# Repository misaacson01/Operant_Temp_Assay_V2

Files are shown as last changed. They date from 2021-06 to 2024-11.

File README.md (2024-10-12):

# Operant_Temp_Assay_V2

This repo contains code and instructions for assembling, installing, and operating the Hoon lab operant temperature apparatus (V2). This is an updated and modified version of the assay originally described by [Isaacson and Hoon, 2021](https://doi.org/10.1177/17448069211013633).

## Hardware assembly
1) Order two recirculating water baths with external recirculation ports, such as [this one](https://www.polyscience.com/products/circulating-baths/refrigeratedheated-circulating-baths/refrigerated-circulator-7-liter-low-profile-sd-20-c).
2) Order all tubing, parts, and electronics according to the [parts list](https://github.com/misaacson01/Operant_Temp_Assay_V2/blob/main/Parts%20List.xlsx).
3) Order all custom 3D printable parts listed in the [parts list](https://github.com/misaacson01/Operant_Temp_Assay_V2/blob/main/Parts%20List.xlsx). Stl files needed to print the parts can be found in the [3D Prints](https://github.com/misaacson01/Operant_Temp_Assay_V2/tree/main/3D%20prints) folder.
    * To order custom prints online, use a 3D print service such as [Craftcloud](https://craftcloud3d.com/) by uploading the .stl files located in the [3D Prints folder](https://github.com/misaacson01/Operant_Temp_Assay_V2/tree/main/3D%20prints).
    * To print the parts yourself, we recommended using an FDM printer such as the [Prusa MK4S](https://www.prusa3d.com/product/original-prusa-mk4s-3d-printer-5/) using PLA filament.
    * Whether going through a service or printing yourself, these are our suggested print parameters:
        * File units: millimeters
        * Printing process type: FDM
        * Material: PLA
        * Infill: 20%
        * Support: none
        * Layer Height: 300 micrometers (or less)
        * Finish: Standard/As printed/No finish
        * Print orientation: default
        * Tolerance: 500 micrometers (or less)
4) Assemble the nose poke detectors
    * Solder the photo interrupter, a 200 Ohm resistor, and ~0.5 m each of 3 hookup wires (red=power, black=ground, and yellow=signal) to the photo interrupter breakout PCB. Repeat this step to create 3 assembled photointerrupter-based nose poke detectors
    * Place each nose poke detector into the matching slots of the Thermobox 3D print. Add a dab of glue to fix the detectors in place
5) Assemble the water bath valves and large tubing
    * Connect 1/4" hose barb connectors to both sides of 2 large solenoid valves (2 valves are used for the two water bath circulating loops)
    * Hook up water baths, large (8 mm ID) tubing, and large valves according to page 1 of the [tubing diagram](https://github.com/misaacson01/Operant_Temp_Assay_V2/blob/main/docs/Thermo%20Assay%20V2%20Diagrams.pptx)
    * Connect the large solenoid valves to power according to page 2 of the [tubing diagram](https://github.com/misaacson01/Operant_Temp_Assay_V2/blob/main/docs/Thermo%20Assay%20V2%20Diagrams.pptx)
6) Assemble the water bath small tubing
    * Using the ThermoTemplate 3D print, wind the copper tubing into the slots of the template to bend the copper tubing into a shape of a regularly-spaced grid. Remove the copper tubing from the template when finished
    * Connect the copper tubing to the small valves according to page 1 of the [tubing diagram](https://github.com/misaacson01/Operant_Temp_Assay_V2/blob/main/docs/Thermo%20Assay%20V2%20Diagrams.pptx)
    * Connect the small tubing to the large tubing according to page 1 of the [tubing diagram](https://github.com/misaacson01/Operant_Temp_Assay_V2/blob/main/docs/Thermo%20Assay%20V2%20Diagrams.pptx), using the reducer adapters (8 mm to 6 mm, 1/4" to 1/8") and tubing (1/4" ID)
    * Connect the small solenoid valves to power according to page 2 of the [tubing diagram](https://github.com/misaacson01/Operant_Temp_Assay_V2/blob/main/docs/Thermo%20Assay%20V2%20Diagrams.pptx)
    * Slide the copper tubing grid into the floor slot of the Thermobox
7) Assemble the liquid reward delivery tubing
    * Connect a water reservoir (e.g. a large syringe tube) to the masteflex tubing
    * Glue the 1/8" to 1/16" adapters to the underside of each of the reward ports, with the smaller (1/16") end pointing up into the port to create a reward spout
    * Mount the water reservoir 6-12" above the height of the reward spouts (liquid rewards are gravity-fed)
    * Connect 1/8" hose barb connectors to both sides of 3 small solenoid valves (3 valves are used for 3 separate reward locations in the Thermobox)
    * Use Tee connectors to split the tubing from the reservoir to connect to one port the 3 small solenoid valves
    * Connect the opposite ports of each small solenoid valve to each of the reward spouts adapters
8) Wire the liquid reward delivery valves (see also page 2 of the [tubing diagram](https://github.com/misaacson01/Operant_Temp_Assay_V2/blob/main/docs/Thermo%20Assay%20V2%20Diagrams.pptx))
    * Using black hookup wire, connect the negative (ground) screw terminal of the 2.1 mm power jack to the center screw terminal of a relay in the relay module
    * Using another black wire, connect the "normally open" screw terminal of the relay to one of the two pins of a small solenoid valve (the wire may need to be soldered to the solenoid valve pin)
    * Using a red wire, connect the other pin of the solenoid valve to the positive (power) screw terminal of the 2.1 mm power jack
    * Solder a diode between the two pins of the small solenoid valve, orienting the diode so that current can flow from the negative pin to the positive pin
    * Repeat these steps for all 3 liquid reward valves
    * Plug in a 12 V (1+ A) power cord to the 2.1 mm power jack
9) (optional) Assemble the LED display boards
    * [displays are deprecated, to be replaced with newer I2C displays such as [this one](https://www.adafruit.com/product/4741)]

## Electronics assembly
[To be added]

## Software Installation

##### Install software on the host PC
1) Install [Matlab](https://www.mathworks.com/products/matlab.html)
2) Download this repository's code (with Github Desktop or your preferred SVN client)
3) Open Matlab and add this repository to the list of paths:
    * In Matlab's "Home" tab, click "Set Path"
    * Click "Add with Subfolders"
    * Navigate to the file location where this repository was downloaded and click on the folder name
    * "Save" and "Close"
4) Install the [Arduino IDE](https://www.arduino.cc/en/software).
5) Open the Arduino IDE, click "Tools", then "Manage libraries". Install the following libraries: Adafruit MAX31856; Adafruit GFX; Adafruit Seesaw; Adafuit ST7735 and ST7789; Adafruit BUSIO

##### Install the Arduino controller firmware
1) Plug in the Arduino microcontroller connected to the apparatus to the host PC.
2) Open the Arduino IDE
3) Select "Arduino Uno" from the microcontroller dropdown menu, and select the port which your Arduino is connected to
    * if you don't know which port the Arduino is on, try disconnecting the Arduino to see which port disappears
4) Download the controller.ino file from the [Arduino](https://github.com/misaacson01/Operant_Temp_Assay_V2/tree/main/Arduino) folder and load it in the Arduino IDE
5) Upload the code to the Arduino

##### Test the software installation
1) In the Matlab command window, type "edit TV2_Test_Experiment"
2) In Matlab's "Editor" tab, click "Run"
3) Watch the command window and the apparatus to check that everything is working correctly

## Running an experiment
To be added

## Troubleshooting
To be added

## Updating Arduino code
To be added

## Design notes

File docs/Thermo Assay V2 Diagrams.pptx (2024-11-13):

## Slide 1

Tubing diagram

Reducer

Large Tee connector

Bloop

Large Tee connector

Big tubing

Water bath B IN

Small tubing

Big valves

Small valves

Bout

Thermo box

Copper tubing

Water bath B OUT

Water bath A IN

T connector

Aout

Reducer

Bin

T connector

Ain

Reducer

Large Tee connector

Aloop

Large Tee connector

Water bath A OUT

Reducer

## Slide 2

Solenoid valve
wiring layout

(All solenoid valves are similarly wired)

+

Solenoid valve

Flyback diode

12 v DC

NO

relay

COM

NC

NO = normally open
COM = common
NC = normally closed

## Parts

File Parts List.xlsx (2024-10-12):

 | Part Name | URL | Catalog # | Supplier | Quantity | Price (each) | Total Cost | Notes
Tubing and valves | Masterflex L/S® Precision Pump Tubing, Platinum-Cured Silicone, L/S 16; 25 ft | https://us.vwr.com/store/item/NA5144597/masterflex-l-s-precision-pump-tubing-platinum-cured-silicone-avantor | MFLX96410-16 | VWR | 1 | $108.00 | $108.00
 | Copper Tubing, 3mm OD, 2mm ID, 16 ft Length | Refrigeration Tubing Copper Tubing Coil 3mm OD x 2mm ID x 24.5Ft Length - Walmart.com - Walmart.com (https://www.walmart.com/ip/Refrigeration-Tubing-Copper-Tubing-Coil-3mm-OD-x-2mm-ID-x-24-5Ft-Length/426649156?wmlspartner=wmtlabs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) |  | Walmart | 1 | $17.32 | $17.32
 | 8 mm ID Tubing, 50 ft length | https://www.mcmaster.com/5233K958/ | 5233K958 | McMaster-Carr | 1 | $91.50 | $91.50
 | 1/8" hose barb Tee connector | https://www.mcmaster.com/91355K57/ | 91355K57 | McMaster-Carr | 2 | $9.78 | $19.56 | qty: 2 packs of 2 (2+2 spare)
 | 8 mm ID tubing Tee connector | https://www.mcmaster.com/2429K56/ | 2429K56 | McMaster-Carr | 5 | $2.42 | $12.10 | qty: 4+spare
 | 1/8" to 1/16" hose barb adapter (for liquid reward port) | https://www.mcmaster.com/5117K52/ | 5117K52 | McMaster-Carr | 1 | $10.98 | $10.98 | qty: 1 pack of 10 (3+7 spare)
 | 1/4" to 1/8" hose barb adapter (for reducer) | https://www.mcmaster.com/91355K31/ | 91355K31 | McMaster-Carr | 1 | $13.26 | $13.26 | qty: pack of 5 (2+3 spare)
 | 8 mm to 6 mm (~1/4") hose barb adapter (for reducer) | https://www.mcmaster.com/5218K434/ | 5218K434 | McMaster-Carr | 3 | $0.58 | $1.74 | qty: 2+spare
 | 1/4" ID tubing (for reducer) | https://www.mcmaster.com/5233K56/ | 5233K56 | McMaster-Carr | 1 | $10.50 | $10.50
 | 1/4" NPT to 8mm ID hose barb adapter | https://www.mcmaster.com/2429K16/ | 2429K16 | McMaster-Carr | 8 | $4.62 | $36.96 | qty: 6+2 spare
 | 1/8" NPT to 1/8" ID hose barb adapter | https://www.mcmaster.com/5463K438/ | 5463K438 | McMaster-Carr | 1 | $14.08 | $14.08 | qty: pack of 10 (8+2 spare)
 | 12VDC 1/4" NPT Electric Solenoid Valve Normally Open (large valves) | https://www.amazon.com/SNS-2WK025-N08-Electric-Solenoid-Normally/dp/B07SPK59LP/ |  | Amazon | 3 | $20.99 | $62.97 | qty: 2+spare
 | 12VDC 1/8" NPT Electric Solenoid Valve Normally Closed (small valves) | https://www.amazon.com/Brass-Electric-Solenoid-Normally-Closed/dp/B01M5IXT4D/ |  | Amazon | 8 | $7.86 | $62.88 | qty: 7+spare
Electronics | SainSmart 8-Channel Relay Module | https://www.amazon.com/SainSmart-101-70-102-8-Channel-Relay-Module/dp/B0057OC5WK | B0057OC5WK | Amazon | 1 | $11.99 | $11.99
 | Photo Interrupter - GP1A57HRJ00F | https://www.sparkfun.com/products/9299 | SEN-09299 | Sparkfun | 4 | $2.50 | $10.00 | qty: 3+spare
 | SparkFun Photo Interrupter Breakout Board - GP1A57HRJ00F | https://www.sparkfun.com/products/9322 | BOB-09322 | Sparkfun | 4 | $1.50 | $6.00 | qty: 3+spare
 | Hook-up Wire - Black (22 AWG) | https://www.sparkfun.com/products/8022 | PRT-08022 | Sparkfun | 1 | $2.50 | $2.50
 | Hook-up Wire - Red (22 AWG) | https://www.sparkfun.com/products/8023 | PRT-08023 | Sparkfun | 1 | $2.50 | $2.50
 | Hook-up Wire - Yellow (22 AWG) | https://www.sparkfun.com/products/8024 | PRT-08024 | Sparkfun | 1 | $2.50 | $2.50
 | Adafruit METRO 328 - Arduino Compatible - with Headers - ATmega328 | https://www.adafruit.com/product/2488 | 2488 | Adafruit | 1 | $17.50 | $17.50
 | Proto-Screwshield (Wingshield) R3 Kit for Arduino | https://www.adafruit.com/product/196 | 196 | Adafruit | 1 | $14.95 | $14.95
 | (optional display) 2.2" 18-bit color TFT LCD display with microSD card breakout | https://www.adafruit.com/product/1480 | 1480 | Adafruit | 2 | $24.95 | $49.90
 | (optional display controller) Adafruit Metro Mini 328 - Arduino-Compatible - 5V 16MHz | https://www.adafruit.com/product/2590 | 2590 | Adafruit | 2 | $12.50 | $25.00
 | Adafruit Universal Thermocouple Amplifier MAX31856 Breakout | https://www.adafruit.com/product/3263 | 3263 | Adafruit | 1 | $17.50 | $17.50
 | Thermocouple Type-K Glass Braid Insulated - K | https://www.adafruit.com/product/270 | 270 | Adafruit | 2 | $9.95 | $19.90 | qty: 1+spare
 | Premium Female/Male 'Extension' Jumper Wires - 40 x 6" (150mm) | https://www.adafruit.com/product/826 | 826 | Adafruit | 1 | $3.95 | $3.95
 | 12V 5A switching power supply | https://www.adafruit.com/product/352 | 352 | Adafruit | 1 | $24.95 | $24.95
 | Female DC Power adapter - 2.1mm jack to screw terminal block | https://www.adafruit.com/product/368 | 368 | Adafruit | 1 | $2.00 | $2.00
 | USB cable - USB A to Micro-B - 3 foot long | https://www.adafruit.com/product/592 | 592 | Adafruit | 4 | $2.95 | $11.80
 | USB Mini Hub with Power Switch | https://www.adafruit.com/product/2998 | 2998 | Adafruit | 1 | $4.95 | $4.95
Test Chamber | Plymor Clear Acrylic Square Polished Edge Display Base, 0.25" H x 4" W x 4" D | https://www.amazon.com/Plymor-Acrylic-Polished-Display-Base-25/dp/B013ITD132 | B013ITD132 | Amazon | 1 | $8.46 | $8.46
 | 3D prints - Test Chamber, Catch Tray, Tube Template | https://craftcloud3d.com/ | - | Craftcloud3d | 1 | $50.00 | $50.00 | cost estimate
 |  |  |  |  |  | Total | $748.20

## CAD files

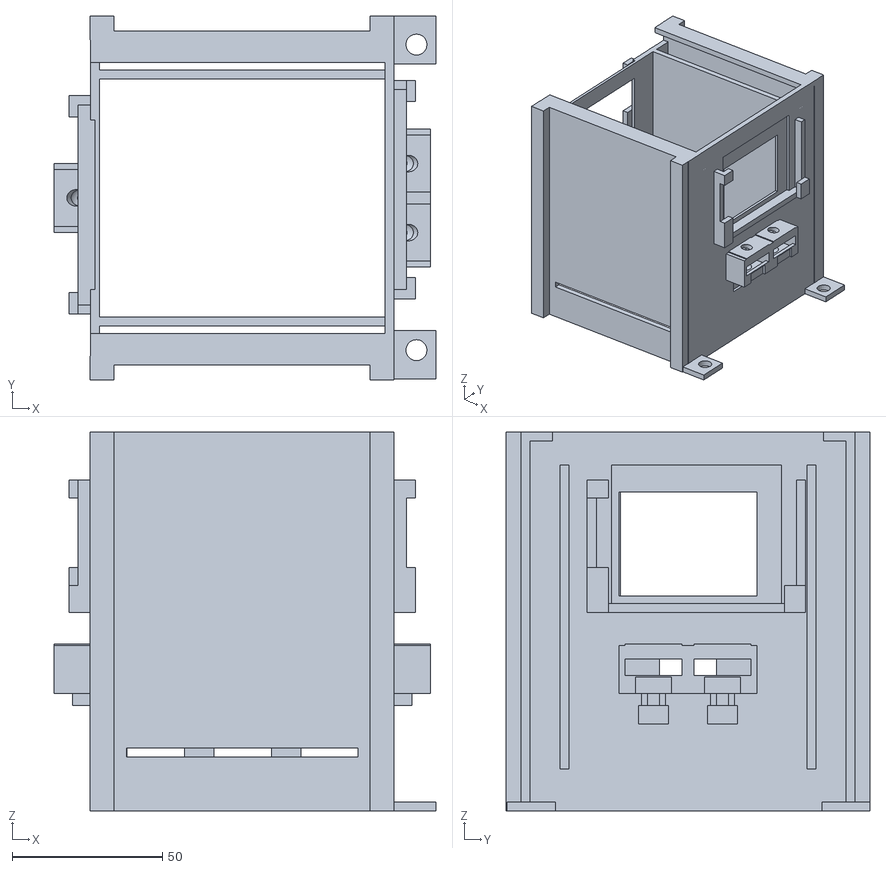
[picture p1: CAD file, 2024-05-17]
3D prints/ThermoBox/ThermoBox.stl
127.0 x 121.0 x 126.0

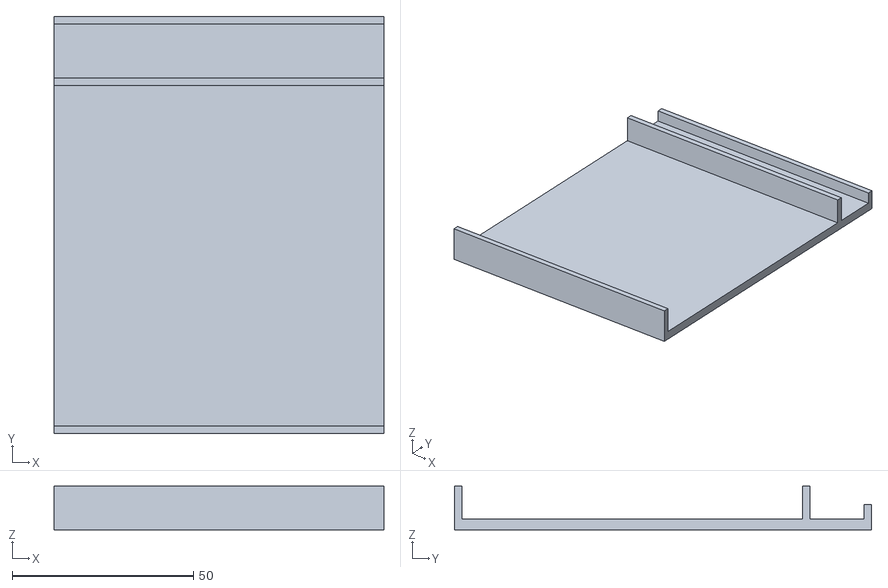
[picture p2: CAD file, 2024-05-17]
3D prints/ThermoCatch/tinker.obj
91.0 x 115.0 x 12.0

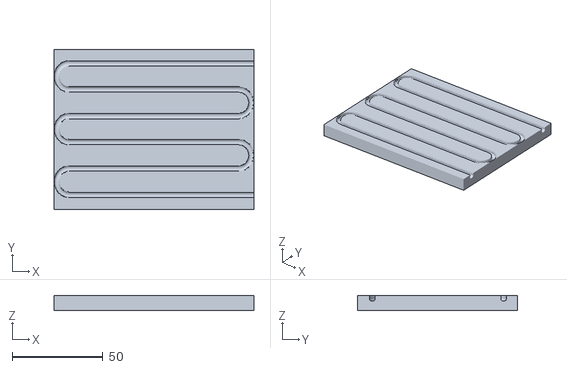
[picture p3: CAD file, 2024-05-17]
3D prints/ThermoTemplate/tinker.obj
110.0 x 88.0 x 8.00

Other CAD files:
3D prints/ThermoBox/tinker.obj
3D prints/ThermoCatch/ThermoCatch.stl
3D prints/ThermoTemplate/ThermoTemplate.stl

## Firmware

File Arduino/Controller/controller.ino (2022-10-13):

//set program ID
uint16_t programIDint = 1000; //controller 1000 (thermoV2 controller)
uint8_t programNum = 1; //controller #1
uint8_t versionID = 1; //V1

bool rundemo = 0; //for testing displays without scripts

//include necessary libraries
#include "SPI.h"
#include <Adafruit_MAX31856.h>

//pinouts
uint8_t relayPins[8] = {2, 3, 4, 5, 6, 7, 8, 9};
uint8_t sensorPins[3] {A0, A1, A2};
#define CS 10 //chip-select
//#define TFT_MOSI 11 //no need to define SPI pins unless you use non-hardware SPI pins
//#define TFT_MISO 12
//#define TFT_CLK 13
Adafruit_MAX31856 maxthermo = Adafruit_MAX31856(CS);

typedef union {
  float floatingPoint;
  byte binary[4];
} binaryFloat;

typedef union {
  int integer;
  byte binary[2];
} binaryInt;

typedef union {
  long longInteger;
  byte binary[4];
} binaryLong;

//initialize variables
uint8_t pin, commandID, fault, tmp;
int sensorVal;
float curtemp;
binaryLong curT, timestamp;
binaryFloat dur, temp;
binaryInt programID, absoluteSensorVal;
long startTime;
int i, j;
int readDelay = 10;
bool endCommand = 0;


//setup (runs once)
void setup() {
  programID.integer = programIDint;
  Serial.begin(115200);

  //set output pins
  for (i=0;i<8;i++) {
      pinMode(relayPins[i], OUTPUT);
      delay(1);
      digitalWrite(relayPins[i], HIGH); //HIGH = off
  }

  //initialize thermocouple
  if (!maxthermo.begin()) {
    Serial.println("Could not initialize thermocouple.");
    while (1) delay(10);
  }
  maxthermo.setThermocoupleType(MAX31856_TCTYPE_K);
}


//wait for desired amount of available serial data bytes
void wait4Serial(int wait, int num2wait4) {
  while (Serial.available()<num2wait4) {
    delay(wait);
  }
}

bool check4end() {
  //end current command if stop command is recieved
  endCommand = 0;
  if (Serial.available()>0) {
    if (Serial.peek()==200) {
      endCommand = 1;
      commandID = Serial.read();
      Serial.write(commandID);
      timestamp.longInteger = millis();
      Serial.write(timestamp.binary,4);
    } 
  }
  //end pattern if duration is reached
  if ((dur.floatingPoint>0) && ((millis()-startTime)>=(dur.floatingPoint*1000)-1)) {
    endCommand = 1;
  }
  return endCommand;
}
void runDemo() {
  while (1) { //repeat indefinitely

    Serial.println("Testing relays");
    Serial.print("Pins: ");
    for (i=0;i<8;i++) {
      digitalWrite(relayPins[i], LOW);
      Serial.print(relayPins[i]);
      Serial.print(" ");
      delay(500);
      digitalWrite(relayPins[i], HIGH);
    }
    Serial.println("");
    
    Serial.println("Testing sensors");
    Serial.print("Pins: ");
    for (i=0;i<3;i++) {
      sensorVal = analogRead(sensorPins[i]);
      Serial.print(sensorPins[i]);
      Serial.print(": ");
      Serial.print(sensorVal);
      Serial.print("    ");
    }
    Serial.println("");
    delay(1000);
  }
}


void loop() { //main program loop
  if (rundemo==1) {runDemo();} //self-explanatory, right?
  
  //wait for incoming instructions over serial connection
  wait4Serial(readDelay, 1); //wait for (at least) 1 available byte
  
  //read incoming command and data over serial
  commandID = Serial.read(); //read incoming message ID byte (specifies what data is coming next)
  switch (commandID) {
    case 0: //command to send version ID back over serial
      Serial.write(commandID);
      Serial.write(programID.binary,2); //send program ID as 2 bytes
      Serial.write(programNum);
      Serial.write(versionID);
      break;
      
    case 1: //send timestamp
      Serial.write(commandID);
      timestamp.longInteger = millis();
      Serial.write(timestamp.binary,4);
      break;
      
    case 120: //command to toggle a relay for a set duration
      wait4Serial(readDelay, 5); //wait for 5 available bytes

      //read parameters
      dur.binary[0] = Serial.read(); //byte 1
      dur.binary[1] = Serial.read(); //byte 2
      dur.binary[2] = Serial.read(); //byte 3
      dur.binary[3] = Serial.read(); //byte 4
      pin = Serial.read(); //byte 5
      
      //send pattern parameters back for verification
      Serial.write(commandID);
      timestamp.longInteger = millis();
      Serial.write(timestamp.binary,4);
      Serial.write(dur.binary,4);
      Serial.write(pin);

      digitalWrite(relayPins[pin], LOW);
      delay(1000*dur.floatingPoint);
      digitalWrite(relayPins[pin], HIGH);
      break;

    case 121: //comand to read the temperature for a set duration
      wait4Serial(readDelay, 4); //wait for 4 available bytes

      //read parameters
      dur.binary[0] = Serial.read(); //byte 1
      dur.binary[1] = Serial.read(); //byte 2
      dur.binary[2] = Serial.read(); //byte 3
      dur.binary[3] = Serial.read(); //byte 4

      //send parameters back for verification
      Serial.write(commandID);
      timestamp.longInteger = millis();
      Serial.write(timestamp.binary,4);
      Serial.write(dur.binary,4);

      startTime = millis();
      curT.longInteger = 0;
      endCommand = 0;
      while (endCommand==0) {
        curT.longInteger=millis();
        curtemp = maxthermo.readThermocoupleTemperature();
        temp.floatingPoint = curtemp;
        Serial.write(151); //ID for temperature reading
        Serial.write(curT.binary,4);
        Serial.write(temp.binary,4);
        endCommand = check4end();
        delay(100);
      }
      fault = maxthermo.readFault();
      if (fault) {
        curT.longInteger=1000*(millis()-startTime);
        Serial.write(255);
        Serial.write(curT.binary,4);
        if (fault & MAX31856_FAULT_CJRANGE) Serial.println("Cold Junction Range Fault");
        if (fault & MAX31856_FAULT_TCRANGE) Serial.println("Thermocouple Range Fault");
        if (fault & MAX31856_FAULT_CJHIGH)  Serial.println("Cold Junction High Fault");
        if (fault & MAX31856_FAULT_CJLOW)   Serial.println("Cold Junction Low Fault");
        if (fault & MAX31856_FAULT_TCHIGH)  Serial.println("Thermocouple High Fault");
        if (fault & MAX31856_FAULT_TCLOW)   Serial.println("Thermocouple Low Fault");
        if (fault & MAX31856_FAULT_OVUV)    Serial.println("Over/Under Voltage Fault");
        if (fault & MAX31856_FAULT_OPEN)    Serial.println("Thermocouple Open Fault");
      }
      break;

    case 122: //command to read the sensors for a set duration, until the first detection, or until stop command
      wait4Serial(readDelay, 4); //wait for 4 available bytes

      //read parameters
      dur.binary[0] = Serial.read(); //byte 1
      dur.binary[1] = Serial.read(); //byte 2
      dur.binary[2] = Serial.read(); //byte 3
      dur.binary[3] = Serial.read(); //byte 4

      //send pattern parameters back for verification
      Serial.write(commandID);
      timestamp.longInteger = millis();
      Serial.write(timestamp.binary,4);
      Serial.write(dur.binary,4);

      startTime = millis();
      curT.longInteger = 0;
      endCommand=0;
      while (endCommand==0) {
        curT.longInteger=millis();
        for (i=0;i<3;i++) {
          sensorVal = analogRead(sensorPins[i]);
          if (sensorVal<512) {
            Serial.write(152);
            Serial.write(curT.binary,4);
            Serial.write(i);
            endCommand=1;
            break;
          }
        }
        delay(2);
        if (endCommand==0) {
          endCommand = check4end();
        }
      }
      break;

    case 123: //get absolute sensor readings
      Serial.write(commandID);
      timestamp.longInteger = millis();
      Serial.write(timestamp.binary,4);
      for (j=0;j<5;j++) {
        for (i=0;i<3;i++) {
          absoluteSensorVal.integer = analogRead(sensorPins[i]);
          Serial.write(153);
          Serial.write(absoluteSensorVal.binary,2);
          Serial.write(byte(i));
        }
        delay(1000);
      }
      break;
      
    case 200: //stop command recieved
      Serial.write(commandID);
      timestamp.longInteger = millis();
      Serial.write(timestamp.binary,4);
      break;

      
    default: //send back unknown command
      Serial.write(commandID);
      timestamp.longInteger = millis();
      Serial.write(timestamp.binary,4);
      Serial.print("unknown bytes: ");
      while (Serial.available()>0) {
        tmp = Serial.read();
        Serial.print(tmp);
        Serial.print(" ");
      }
      Serial.print("\n");
      break;
  }
}
//loop end

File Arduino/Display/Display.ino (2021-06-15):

//set program ID
uint16_t programIDint = 9340; //ILI9340-based display
uint8_t programNum = 1; //controller #
uint8_t versionID = 1; 

bool rundemo = 0; //for testing displays without scripts

//define pinouts
#define BACKLIGHT 6 //pin which controls the display backlight
#define TRIG_IN 0 //pin which reads input trigger signals
#define TRIG_OUT 1 //pin which sets an output trigger signal
#define TFT_DC 8 //Data/command
#define TFT_CS 10 //chip-select
#define TFT_RST 9 //reset
//#define TFT_MOSI 11 //no need to define SPI pins unless you use non-hardware SPI pins
//#define TFT_MISO 12
//#define TFT_CLK 13

//include necessary libraries
#include "SPI.h"
#include <Adafruit_GFX.h>        // Core graphics library
#include <Adafruit_ILI9341.h>      // Hardware-specific driver library

//create TFT object
Adafruit_ILI9341 tft = Adafruit_ILI9341(TFT_CS, TFT_DC); 

//create byte/float and byte/int16 unions
typedef union {
  float floatingPoint;
  byte binary[4];
} binaryFloat;

typedef union {
  int integer;
  byte binary[2];
} binaryInt;

typedef union {
  long longInteger;
  byte binary[4];
} binaryLong;

//initialize pattern parameters
uint8_t commandID, numRepeats, gratingType, wait4trig, tmp;
binaryFloat r1, r2, r3, g1, g2, g3, b1, b2, b3; //R, G, B color values will be 0-1 floats, transferred as bytes
binaryInt xCenter, yCenter, patternWidth, patternHeight, angle, barWidth; //int16s, transferred as bytes
binaryFloat freq, dur, pre; //floats, transferred as bytes

//initialize other common variables
int w, h, x, y, c, on, i, x0, y0, x1, y1, blx, bly, curX, curY, xHeight, xWidth, yHeight, yWidth, displayHeight, displayWidth, bigWidth;
int barWidthLines, bar, numLines, numAddedLines, startLine, nextLine, addedDirection, startC, L, xDir, yDir;
bool xShift[600];
int readDelay = 10;
uint16_t color1, color2, color3, color3_old, colors[3]; //16-bit colors
bool endPattern = 0;
bool backlightState = LOW;
bool xBigger;
long startTime, displayTime, onTime;
unsigned long frameUs, lineUs, startUs, durUs, shiftUs;
double radius;
float slope, blAngle;
float pi = 3.14159;
binaryLong timestamp;
binaryInt programID;


/////////setup (runs once)
void setup() {
  Serial.begin(115200);
  pinMode(BACKLIGHT, OUTPUT);
  pinMode(TRIG_IN, INPUT);
  pinMode(TRIG_OUT, OUTPUT);
  digitalWrite(BACKLIGHT, LOW);
  digitalWrite(TRIG_OUT, LOW);
  digitalWrite(TFT_RST, HIGH);
  tft.begin();
  delay(100);

  programID.integer = programIDint;

  tft.setRotation(3); // for displays mounted sideways, with pins on the left
  displayWidth = tft.width(); // width of display in pixels
  displayHeight = tft.height(); // height of display in pixels
  tft.fillScreen(ILI9341_BLACK);
}

/////////create other small functions
//convert 0-1 RGB values to 16-bit color
uint16_t RGBto16(float R, float G, float B) {
  uint8_t r = round(R*31); //red gets 5 bits
  uint8_t g = round(G*63); //green gets 6 bits
  uint8_t b = round(B*31); //blue gets 5 bits
  uint16_t c = r; //add red to lowest 5 bits 
  c = c<<6; //shift over by 6 bits to make room for green
  c |= g; //add green to lowest 6 bits 
  c = c<<5; //shift over by 5 bits to make room for blue
  c |= b; //add blue to lowest 5 bits 
  return c;
}

//wait for desired amount of available serial data bytes
void wait4Serial(int wait, int num2wait4) {
  while (Serial.available()<num2wait4) {
    delay(wait);
  }
}

//convert degrees to radians
float deg2rad(float deg) {
  return (deg*pi/180); //convert degrees to radians
}

//convert degrees to radians
float rad2deg(float rad) {
  return ((rad*180)/pi); //convert degrees to radians
}


bool check4end() {
  //end pattern if stop command is recieved
  endPattern = 0;
  if (Serial.available()>0) {
    if (Serial.peek()==200) {
      endPattern = 1;
      commandID = Serial.read();
      Serial.write(commandID);
      timestamp.longInteger = millis();
      Serial.write(timestamp.binary,4);
    } 
  }
  //end pattern if duration is reached
  if ((dur.floatingPoint>0) && ((millis()-startTime)>=(dur.floatingPoint*1000)-1)) {
    endPattern = 1;
  }
  return endPattern;
}


//run display demo without needing PC input (set rundemo=1)
void runDemo() {
  while (1) { //repeat indefinitely
    Serial.println("Beginning fast V lines");
    digitalWrite(BACKLIGHT, HIGH);
    startTime = millis();
    for (x=0;x<displayWidth;x++) {
      tft.drawFastVLine(x, 0, displayHeight, 15);
    }
    for (x=0;x<displayWidth;x++) {
      tft.drawFastVLine(x, 0, displayHeight, 0);
    }
    digitalWrite(BACKLIGHT, LOW);
    displayTime = millis()-startTime;
    Serial.print("elapsed time: ");
    Serial.print((displayTime));
    Serial.println("ms");
    delay(2000);
  }
}
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

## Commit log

2021-06-15 Added files for alternate control strategy
    [Parts List.xlsx]
2022-10-07 Added command for testing sensors (get absolute sensor readings)
2024-05-17 Added 3D print files
    [ThermoBox.stl, ThermoCatch.stl, ThermoTemplate.stl, tinker.obj]
2024-10-11 Update Parts List.xlsx
    [Parts List.xlsx]
2024-10-12 Updated tubing and valves
    [Parts List.xlsx]
2024-11-13 Added relay details in valve wiring diagram
